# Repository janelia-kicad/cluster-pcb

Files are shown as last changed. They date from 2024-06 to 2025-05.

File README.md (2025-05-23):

- [Repository Info](#orgbacf8f6)
- [Images](#org53d800a)
- [Schematic](#org38f91d3)
- [PCB](#org650b85d)
- [Bill of Materials](#org1cf7621)
- [Development](#org0d98822)

    <!-- This file is generated automatically from metadata -->
    <!-- File edits may be overwritten! -->

# Repository Info

-   Project Name: cluster-pcb
-   Synopsis: PCB for each cluster of prisms in the Voigts Lab honeycomb maze.
-   Documentation Version: 2.1.0
-   Pcb Version: 2.1
-   Enclosure Version: 1.0
-   Supplemental BOM Version: 2.1.0
-   Release Date: 2025-05-23
-   Creation Date: 2024-06-28
-   Kicad Version: 9.0
-   License: BSD-3-Clause
-   URL: <https://github.com/janelia-kicad/cluster-pcb>
-   Author: Peter Polidoro
-   Email: peter@polidoro.io
-   Copyright: 2025 Howard Hughes Medical Institute
-   References:
    -   <https://github.com/janelia-kicad/prism-pcb>
    -   [W5500-EVB-Pico](https://docs.wiznet.io/Product/iEthernet/W5500/w5500-evb-pico)

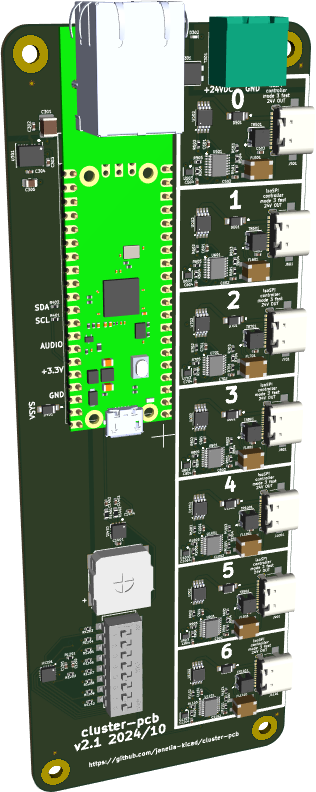
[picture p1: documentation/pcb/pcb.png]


# Images

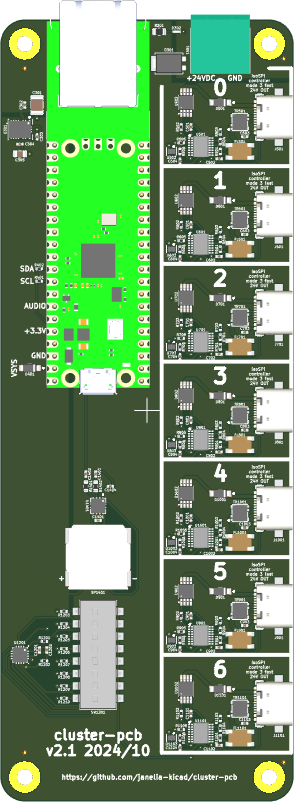
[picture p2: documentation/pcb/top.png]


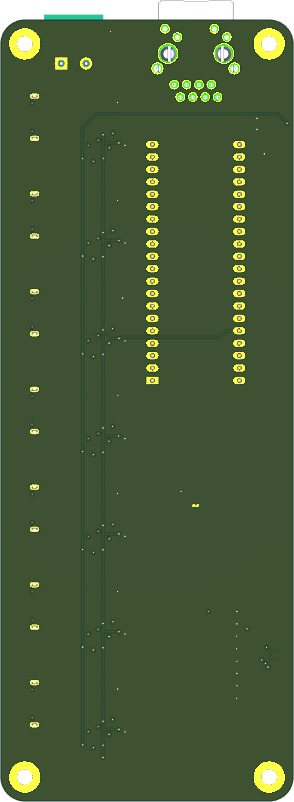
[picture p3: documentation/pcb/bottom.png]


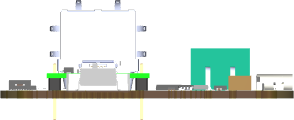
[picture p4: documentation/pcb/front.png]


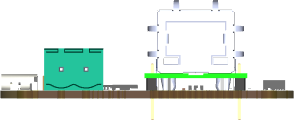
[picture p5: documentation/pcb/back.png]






# Schematic

[./documentation/schematic/cluster-pcb.pdf](./documentation/schematic/cluster-pcb.pdf)





























# PCB











# Bill of Materials

## Board

| Item | Synopsis                                  | Manufacturer Part Number | Manufacturer                         | Quantity | Reference(s)                                                                                                                    | Package            |
|---- |----------------------------------------- |------------------------ |------------------------------------ |-------- |------------------------------------------------------------------------------------------------------------------------------- |------------------ |
| 1    | 50V 3.3uF                                 | FS32X335K500EGG          | PSA(Prosperity Dielectrics)          | 1        | C301                                                                                                                            | 1210               |
| 2    | CAP CER 0.1UF 100V X5R                    | GRM155R62A104KE14D       | Murata Electronics                   | 24       | C302 C501 C502 C504 C601 C602 C604 C701 C702 C704 C801 C802 C804 C901 C902 C904 C1001 C1002 C1004 C1101 C1102 C1104 C1201 C1202 | 0402               |
| 3    | CAP CER 1UF 25V X5R                       | GRT155R61E105KE01D       | Murata Electronics                   | 2        | C303 C304                                                                                                                       | 0402               |
| 4    | CAP CER 47UF 10V X5R                      | CGA0805X5R476M100MT      | HRE                                  | 1        | C305                                                                                                                            | 0805               |
| 5    | CAP CER 27pF 50V 5%                       | 0402CG270J500NT          | FH (Guangdong Fenghua Advanced Tech) | 7        | C503 C603 C703 C803 C903 C1003 C1103                                                                                            | 0402               |
| 6    | CAP CER 1UF 35V X5R                       | CL05A105KL5NRNC          | Samsung Electro-Mechanics            | 1        | C1401                                                                                                                           | 0402               |
| 7    | CAP CER 0.22UF 25V X6S                    | GRT155C81E224KE01D       | Murata Electronics                   | 3        | C1402 C1403 C1404                                                                                                               | 0402               |
| 8    | 50V 15A PowerDI-5 Super Barrier Rectifier | SBRT15U50SP5-13          | Diodes Incorporated                  | 1        | D301                                                                                                                            | PowerDI-5          |
| 9    | LED RED CLEAR CHIP SMD                    | APHHS1005SURCK           | Kingbright                           | 1        | D302                                                                                                                            | 0402               |
| 10   | DIODE SCHOTTKY 20V 1A                     | MBR120VLSFT1G            | onsemi                               | 8        | D401 D501 D601 D701 D801 D901 D1001 D1101                                                                                       | SOD-123FL          |
| 11   | CMC 22UH 200MA 2LN 1.2KOHM SMD            | ACT45B-220-2P-TL003      | TDK                                  | 7        | FL501 FL601 FL701 FL801 FL901 FL1001 FL1101                                                                                     | 1812               |
| 12   | USB Type-C 2.0 16P 5A                     | GT-USB-7047C             | G-Switch                             | 7        | J501 J601 J701 J801 J901 J1001 J1101                                                                                            | SMD                |
| 13   | RA73F 2A 2K32 0.1% 5K RL                  | RA73F2A2K32BTD           | TE Connectivity Passive Product      | 1        | R301                                                                                                                            | 0805               |
| 14   | RES SMD 1.8K OHM 5% 100mW                 | ERJ2GEJ182X              | PANASONIC                            | 16       | R401 R402 R505 R506 R605 R606 R705 R706 R805 R806 R905 R906 R1005 R1006 R1105 R1106                                             | 0402               |
| 15   | RES SMD 100 OHM 1% 62.5mW                 | 0402WGF1000TCE           | UNI-ROYAL(Uniroyal Elec)             | 7        | R501 R601 R701 R801 R901 R1001 R1101                                                                                            | 0402               |
| 16   | RES SMD 4.7K OHM 1% 6.25mW                | 0402WGF4701TCE           | UNI-ROYAL(Uniroyal Elec)             | 7        | R502 R602 R702 R802 R902 R1002 R1102                                                                                            | 0402               |
| 17   | RES SMD 1.4K OHM 1% 62.5mW                | RC0402FR-071K4L          | YAGEO                                | 7        | R503 R603 R703 R803 R903 R1003 R1103                                                                                            | 0402               |
| 18   | RES SMD 604 OHM 1% 100mW                  | ERJ2RKF6040X             | PANASONIC                            | 7        | R504 R604 R704 R804 R904 R1004 R1104                                                                                            | 0402               |
| 19   | RES SMD 10K OHM 5% 1/10W                  | ERJ2GEJ103X              | PANASONIC                            | 10       | R1201 R1202 R1203 R1204 R1205 R1206 R1207 R1208 R1209 R1210                                                                     | 0402               |
| 20   | RES SMD 40k OHM 1% 100mW                  | SCR0603F40K              | VO                                   | 2        | R1401 R1402                                                                                                                     | 0603               |
| 21   | SPEAKER 8OHM 700MW                        | KLJ-01304T-08R07W        | KELIKING                             | 1        | SP1401                                                                                                                          |                    |
| 22   | SWITCH SLIDE DIP SPST 0.025A 24V          | SDA08H1SBDR              | C&K                                  | 1        | SW1201                                                                                                                          | SMD                |
| 23   | TERM BLOCK HDR 2POS 90DEG 5.08MM          | 1757242                  | Phoenix Contact                      | 1        | T301                                                                                                                            | Push-Pull P=5.08mm |
| 24   | Pulse Transformer 120uH 1CT:1CT           | FB020G00                 | Dongguan Mentech Optical & Magnetic  | 7        | TR501 TR601 TR701 TR801 TR901 TR1001 TR1101                                                                                     | SMD-6P 3.5x3.2mm   |
| 25   | DC-DC 5V 600mA Output 3-65V Input         | TPSM365R6V5RDNR          | Texas Instruments                    | 1        | U301                                                                                                                            | QFN-11(3.5x4.5)    |
| 26   | SPI Isolator                              | LTC6820HMS#3ZZTRPBF      | Analog Devices                       | 7        | U501 U601 U701 U801 U901 U1001 U1101                                                                                            | MSOP-16            |
| 27   | IC BUFF NON-INVERT 1.65-5.5V              | SN74LVC1G125DRYR         | Texas Instruments                    | 7        | U503 U603 U703 U803 U903 U1003 U1103                                                                                            | USON-6(1x1.5)      |
| 28   | IC XPNDR 400KHZ I2C SMBUS                 | TCA6408ARGTR             | Texas Instruments                    | 1        | U1201                                                                                                                           | QFN-16-EP(3x3)     |
| 29   | IC AMP CLASS AB MONO 1.7W                 | TPA6204A1DRBR            | Texas Instruments                    | 1        | U1401                                                                                                                           | QFN-8-EP(3x3)      |
|      | IC PWR DRIVER N-CHAN 1:1                  |                          | Texas Instruments                    | 7        | U502 U602 U702 U802 U902 U1002 U1102                                                                                            | EMSOP-8-EP         |

## Supplemental

| Item | Synopsis                        | Manufacturer Part Number | Manufacturer    | Quantity | Cost  | Total |
|---- |------------------------------- |------------------------ |--------------- |-------- |----- |----- |
| 1    | TERM BLOCK PLUG 2POS STR 5.08MM | 1758364                  | Phoenix Contact | 1        | 1.63  | 1.63  |
| 2    | CONN FERRULE DIN 16AWG BLACK    | 3200043                  | Phoenix Contact | 4        | 0.14  | 0.56  |
| 3    | POWER CABLE BULK SJT 16/3       | H-137                    | GlobTek, Inc.   | 1        | 2.40  | 2.40  |
| 4    | W5100S-EVB-PICO RP2040 W5100S   | W5100S-EVB-PICO          | WIZnet          | 1        | 9.95  | 9.95  |
| 5    | Supplemental BOM Version: 2.1.0 |                          |                 |          | Total | 14.54 |

# Development

## Install Guix

[Install Guix](https://guix.gnu.org/manual/en/html_node/Binary-Installation.html)

## Generate Output from KiCad

### Remove previous versions

```sh
rm -rf ./documentation/3dmodels/* && rm -rf ./documentation/bom/* && rm -rf ./documentation/fabrication/* && rm -rf ./documentation/pcb/* && rm -rf ./documentation/schematic/*pcb
```

### Images

1.  3D Viewer

    Output directory: ../documentation/pcb
    
    -   pcb.png
    -   top.png
    -   bottom.png
    -   front.png
    -   back.png
    -   left.png
    -   right.png

2.  Trim

        make trimmed-images

3.  Schematic PDF

    File -> Plot
    
    Output directory: ../documentation/schematic
    
    Plot All Pages
    
    -   Output format PDF
    -   Page Size = Schematic size
    -   Plot drawing sheet
    -   Output mode = Color
    -   Color theme = KiCad Default
    -   Default line width = 0.006 in

4.  Schematic SVG

    File -> Plot
    
    Output directory: ../documentation/schematic
    
    Plot All Pages
    
    -   Output format SVG
    -   Page Size = Schematic size
    -   Plot drawing sheet
    -   Output mode = Color
    -   Color theme = Solarized Light
    -   Default line width = 0.012 in

5.  PCB SVG

    Add Edge.Cuts, holes, and dimensions to User.Drawings
    
    File -> Plot
    
    Output directory: ../documentation/pcb
    
    -   Plot format SVG
    -   Include Layers
        -   User.Drawings
        -   F.Silkscreen
        -   B.Silkscreen
        -   F.Fab
        -   B.Fab
    -   Plot on All Layers
        -   Edge.Cuts
    -   Plot footprint values
    -   Plot reference designators
    -   SVG Options
        -   Precision = 4
        -   Output mode = color
    
        make cropped-svg

### Fabrication Files

1.  Gerbers

    File -> Fabrication Outputs -> Gerbers (.gbr)
    
    Output directory: ../documentation/fabrication/gerbers
    
    Include Layers:
    
    -   F.Cu
    -   F.Paste
    -   F.Silks
    -   F.Mask
    -   F.Fab
    -   B.Cu
    -   B.Paste
    -   B.Silks
    -   B.Mask
    -   B.Fab
    -   Edge.Cuts - (contain the board outline/cutouts.)
    -   In1.Cu, In2.Cu … - (needed for 4/6 layer designs.)
    
    Options:
    
    -   Select Plot reference designators, otherwise designators will not appear on silkscreen layers.
    -   Select Check zone fills before plotting
    -   Select Use Protel filename extensions, this is recommended as JLCPCB prefers Protel filename extensions.
    -   Select Subtract soldermask from silkscreen, this ensures no silkscreen on pads.
    -   Coordinate format 4.6 unit mm

2.  Drill and Map Files

    Output directory: ../documentation/fabrication/gerbers
    
    Options:
    
    -   Excellon drill file format
    -   Check Use alternate drill mode for "Oval Holes Drill Mode".
    -   Check Absolute for "Drill Origin".
    -   Check Millimeters for "Drill Units".
    -   Check Decimal format for "Zeros Format".
    -   Gerber X2 map file format
    
    Zip gerber files
    
        zip ./documentation/fabrication/gerbers.zip ./documentation/fabrication/gerbers/*

3.  BOM

    Generate BOM from schematic editor using blank command line to create bom xml file.

4.  POS

    File -> Fabrication Outputs -> Component Placement (.pos)
    
    Output directory: ../documentation/fabrication/
    
    Settings:
    
    -   Format = CSV
    -   Units = Millimeters
    -   Files = Single file for board
    -   Do not use drill/place file origin
    
    Modify pos files:
    
    -   Ref -> Designator
    -   PosX -> Mid X
    -   PosY -> Mid Y
    -   Rot -> Rotation
    -   Side -> Layer

5.  Step

    File -> Export -> Step
    
    Output directory: ../documentation/3dmodels/pcb.step
    
    -   Drill/place file origin
    -   Overwrite old file
    -   Standard Board outline chaining tolerance

## Edit metadata.org

    make metadata-edits

## Tangle metadata.org

    make metadata

## Edit project

    make kicad-edits
    exit

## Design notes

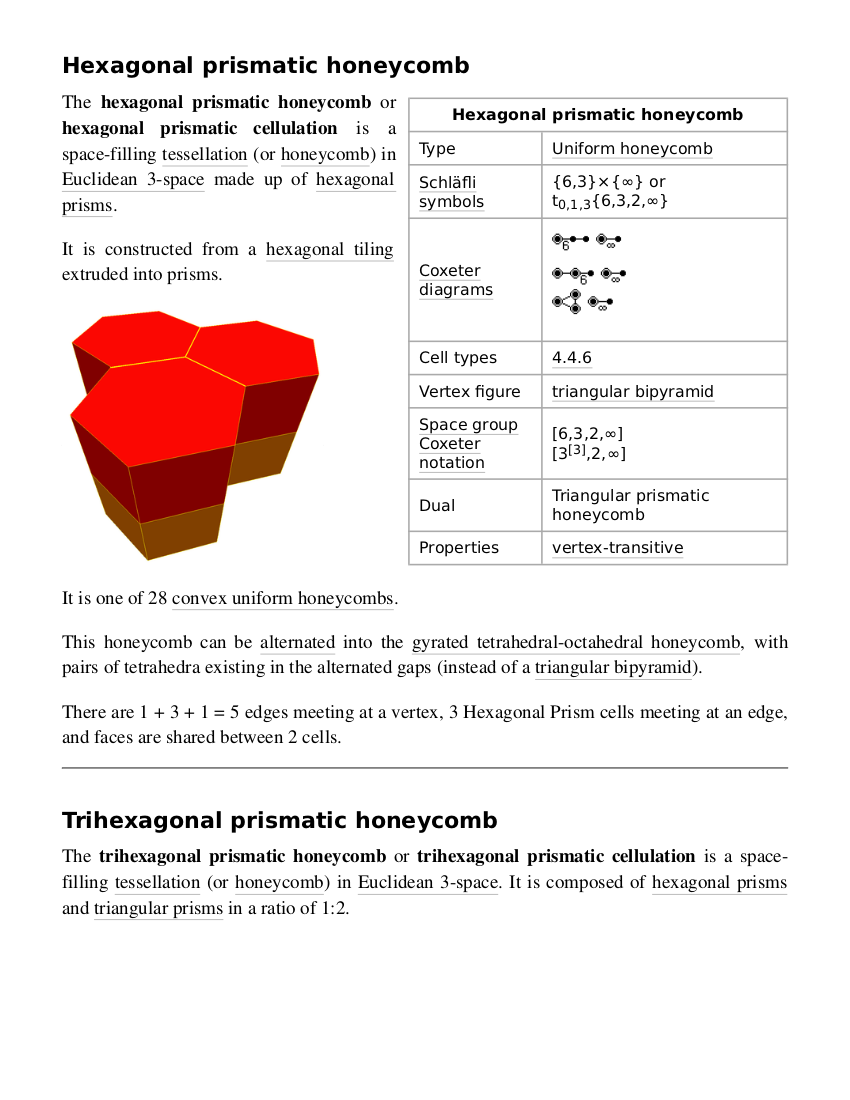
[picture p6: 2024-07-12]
documentation/images/honeycomb.png

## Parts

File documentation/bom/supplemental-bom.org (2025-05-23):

#+OPTIONS: toc:nil title:nil num:nil ^:nil
#+LATEX_HEADER: \usepackage{adjustbox}
#+LATEX_HEADER: \usepackage[margin=2cm]{geometry}
* Supplemental BOM
- Project Name: cluster-pcb
- Synopsis: PCB for each cluster of prisms in the Voigts Lab honeycomb maze.
- Release Date: 2025-05-23
- URL: https://github.com/janelia-kicad/cluster-pcb
- Author: Peter Polidoro
- Email: peter@polidoro.io
#+BEGIN_TABLE
#+LATEX: \adjustbox{max width=\linewidth}{
#+ATTR_LATEX: :center nil
| Item | Synopsis                                               | Manufacturer Part Number | Manufacturer    | Quantity |  Cost | Total |
|------+--------------------------------------------------------+--------------------------+-----------------+----------+-------+-------|
|    1 | TERM BLOCK PLUG 2POS STR 5.08MM                        | 1758364                  | Phoenix Contact |        1 |  1.63 |  1.63 |
|    2 | CONN FERRULE DIN 16AWG BLACK                           | 3200043                  | Phoenix Contact |        4 |  0.14 |  0.56 |
|    3 | POWER CABLE BULK SJT 16/3                              | H-137                    | GlobTek, Inc.   |        1 |  2.40 |  2.40 |
|    4 | W5100S-EVB-PICO RP2040 W5100S                          | W5100S-EVB-PICO          | WIZnet          |        1 |  9.95 |  9.95 |
|------+--------------------------------------------------------+--------------------------+-----------------+----------+-------+-------|
|    5 | Supplemental BOM Version: 2.1.0 |                          |                 |          | Total | 14.54 |
#+TBLFM: $1=@#-1::$7=$5*$6;%0.2f::@>$7=vsum(@2..@-1);%0.2f
#+LATEX: }
#+END_TABLE

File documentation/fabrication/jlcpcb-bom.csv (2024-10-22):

Comment | Designator | Footprint | LCSC
50V 3.3uF | C301 | 1210 | C1021610
CAP CER 0.1UF 100V X5R | C302 C501 C502 C504 C601 C602 C604 C701 C702 C704 C801 C802 C804 C901 C902 C904 C1001 C1002 C1004 C1101 C1102 C1104 C1201 C1202 | 0402 | C162178
CAP CER 1UF 25V X5R | C303 C304 | 0402 | C711085
CAP CER 47UF 10V X5R | C305 | 0805 | C6119904
CAP CER 27pF 50V 5% | C503 C603 C703 C803 C903 C1003 C1103 | 0402 | C1557
CAP CER 1UF 35V X5R | C1401 | 0402 | C307413
CAP CER 0.22UF 25V X6S | C1402 C1403 C1404 | 0402 | C126623
50V 15A PowerDI-5 Super Barrier Rectifier | D301 | PowerDI-5 | C211388
LED RED CLEAR CHIP SMD | D302 | 0402 | C2852592
DIODE SCHOTTKY 20V 1A | D401 D501 D601 D701 D801 D901 D1001 D1101 | SOD-123FL | C223608
CMC 22UH 200MA 2LN 1.2KOHM SMD | FL501 FL601 FL701 FL801 FL901 FL1001 FL1101 | 1812 | C88055
USB Type-C 2.0 16P 5A | J501 J601 J701 J801 J901 J1001 J1101 | SMD | C963218
RA73F 2A 2K32 0.1% 5K RL | R301 | 0805 | C3961061
RES SMD 1.8K OHM 5% 100mW | R401 R402 R505 R506 R605 R606 R705 R706 R805 R806 R905 R906 R1005 R1006 R1105 R1106 | 0402 | C409855
RES SMD 100 OHM 1% 62.5mW | R501 R601 R701 R801 R901 R1001 R1101 | 0402 | C25076
RES SMD 4.7K OHM 1% 6.25mW | R502 R602 R702 R802 R902 R1002 R1102 | 0402 | C25900
RES SMD 1.4K OHM 1% 62.5mW | R503 R603 R703 R803 R903 R1003 R1103 | 0402 | C375491
RES SMD 604 OHM 1% 100mW | R504 R604 R704 R804 R904 R1004 R1104 | 0402 | C2076855
RES SMD 10K OHM 5% 1/10W | R1201 R1202 R1203 R1204 R1205 R1206 R1207 R1208 R1209 R1210 | 0402 | C278577
RES SMD 40k OHM 1% 100mW | R1401 R1402 | 0603 | C3016445
SPEAKER 8OHM 700MW | SP1401 |  | C18186315
SWITCH SLIDE DIP SPST 0.025A 24V | SW1201 | SMD | C2799987
TERM BLOCK HDR 2POS 90DEG 5.08MM | T301 | Push-Pull P=5.08mm | C90074
Pulse Transformer 120uH 1CT:1CT | TR501 TR601 TR701 TR801 TR901 TR1001 TR1101 | SMD-6P 3.5x3.2mm | C19673866
DC-DC 5V 600mA Output 3-65V Input | U301 | QFN-11(3.5x4.5) | C19078014
SPI Isolator | U501 U601 U701 U801 U901 U1001 U1101 | MSOP-16 | C514444
IC BUFF NON-INVERT 1.65-5.5V | U503 U603 U703 U803 U903 U1003 U1103 | USON-6(1x1.5) | C527546
IC XPNDR 400KHZ I2C SMBUS | U1201 | QFN-16-EP(3x3) | C181499
IC AMP CLASS AB MONO 1.7W | U1401 | QFN-8-EP(3x3) | C12400
IC PWR DRIVER N-CHAN 1:1 | U502 U602 U702 U802 U902 U1002 U1102 | EMSOP-8-EP | C2653785

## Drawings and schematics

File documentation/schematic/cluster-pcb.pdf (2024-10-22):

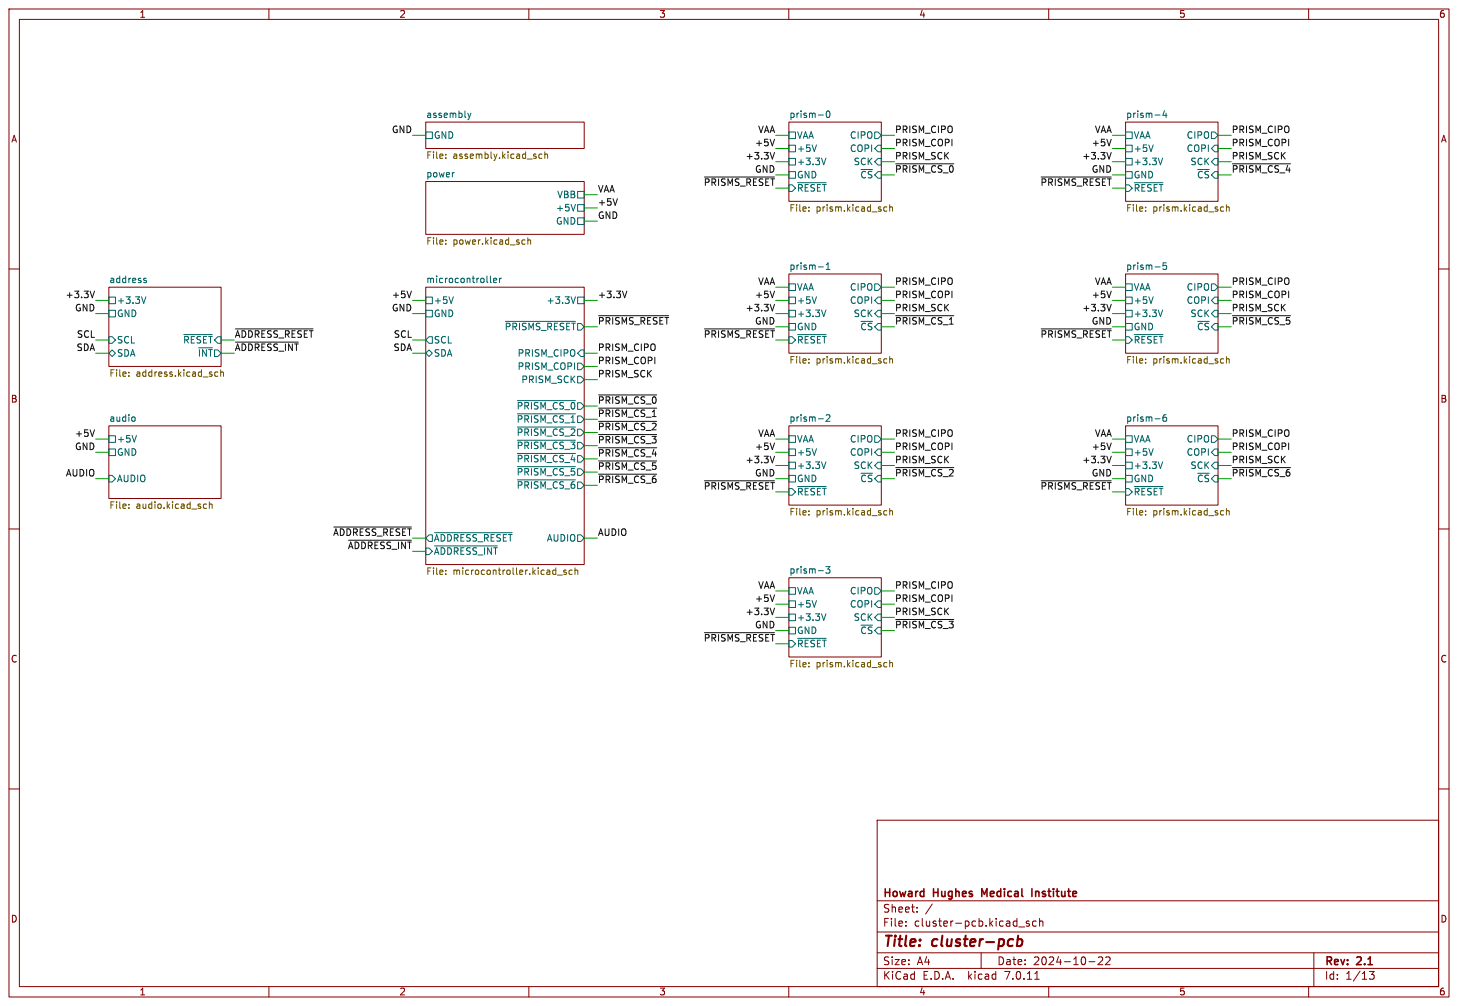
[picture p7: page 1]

~{PRISM_CS_6} microcontroller File: microcontroller.kicad_sch GND

prism-4 File: prism.kicad_sch GND

power File: power.kicad_sch SDA

prism-5 File: prism.kicad_sch GND

prism-3 File: prism.kicad_sch +5V GND

Id: 1/13 Title: cluster-pcb

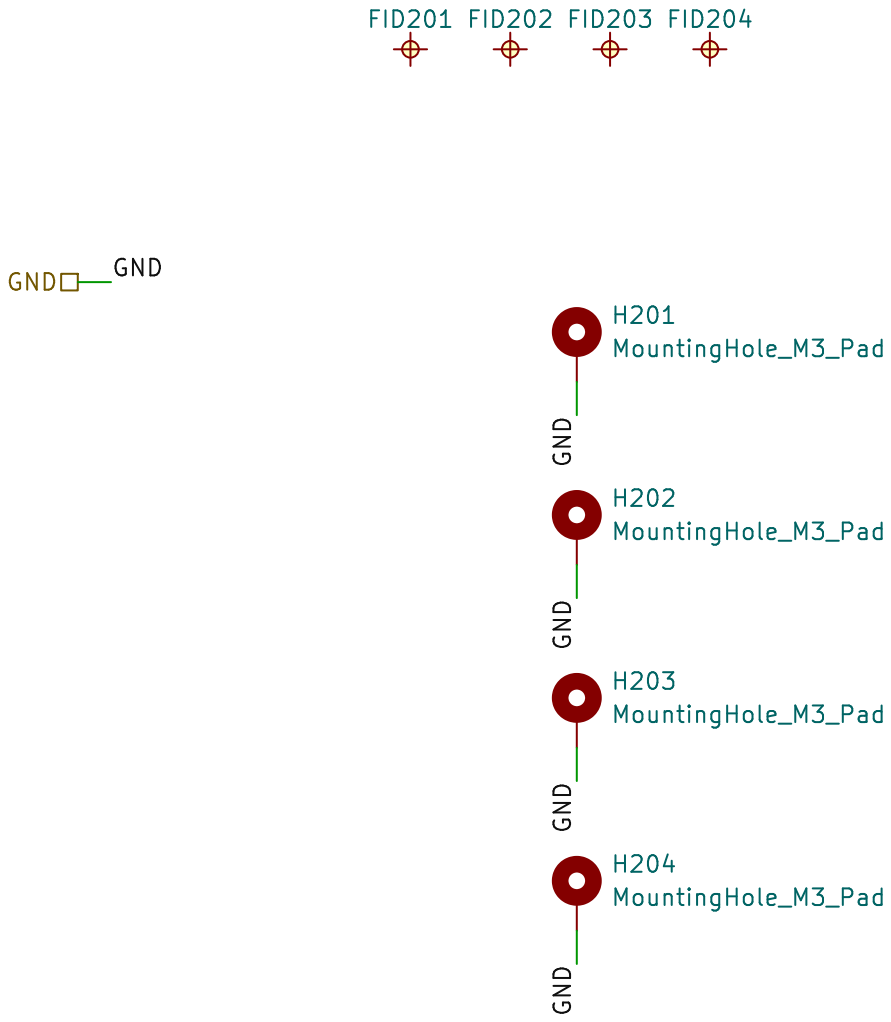
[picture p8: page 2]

Id: 2/13 Title: cluster-pcb

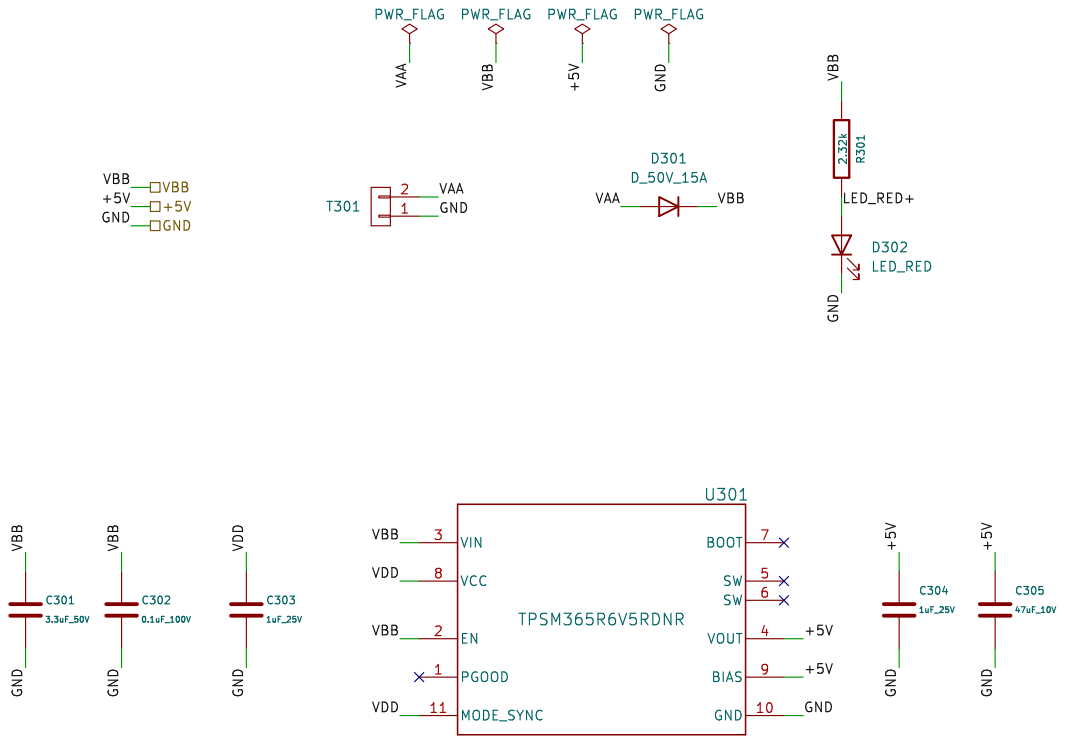
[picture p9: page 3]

Id: 3/13 Title: cluster-pcb

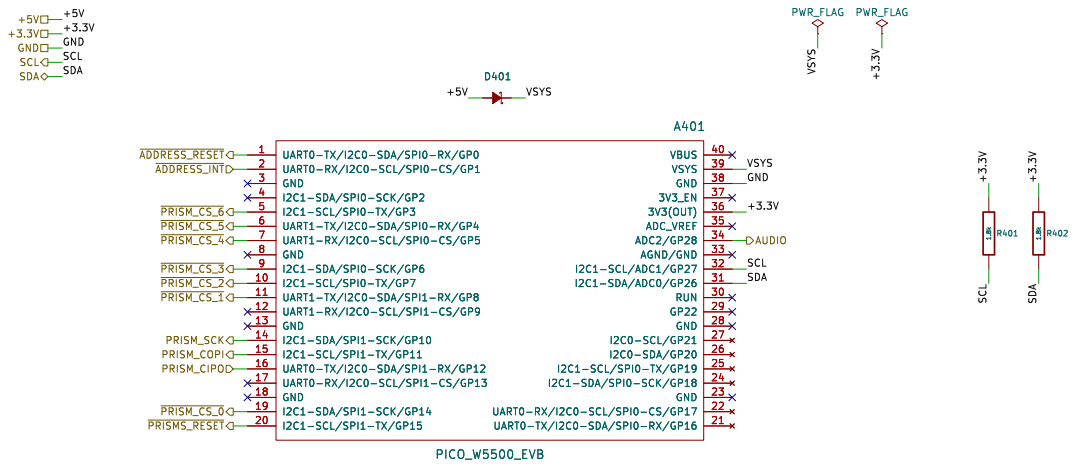
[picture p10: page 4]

Id: 4/13 Title: cluster-pcb

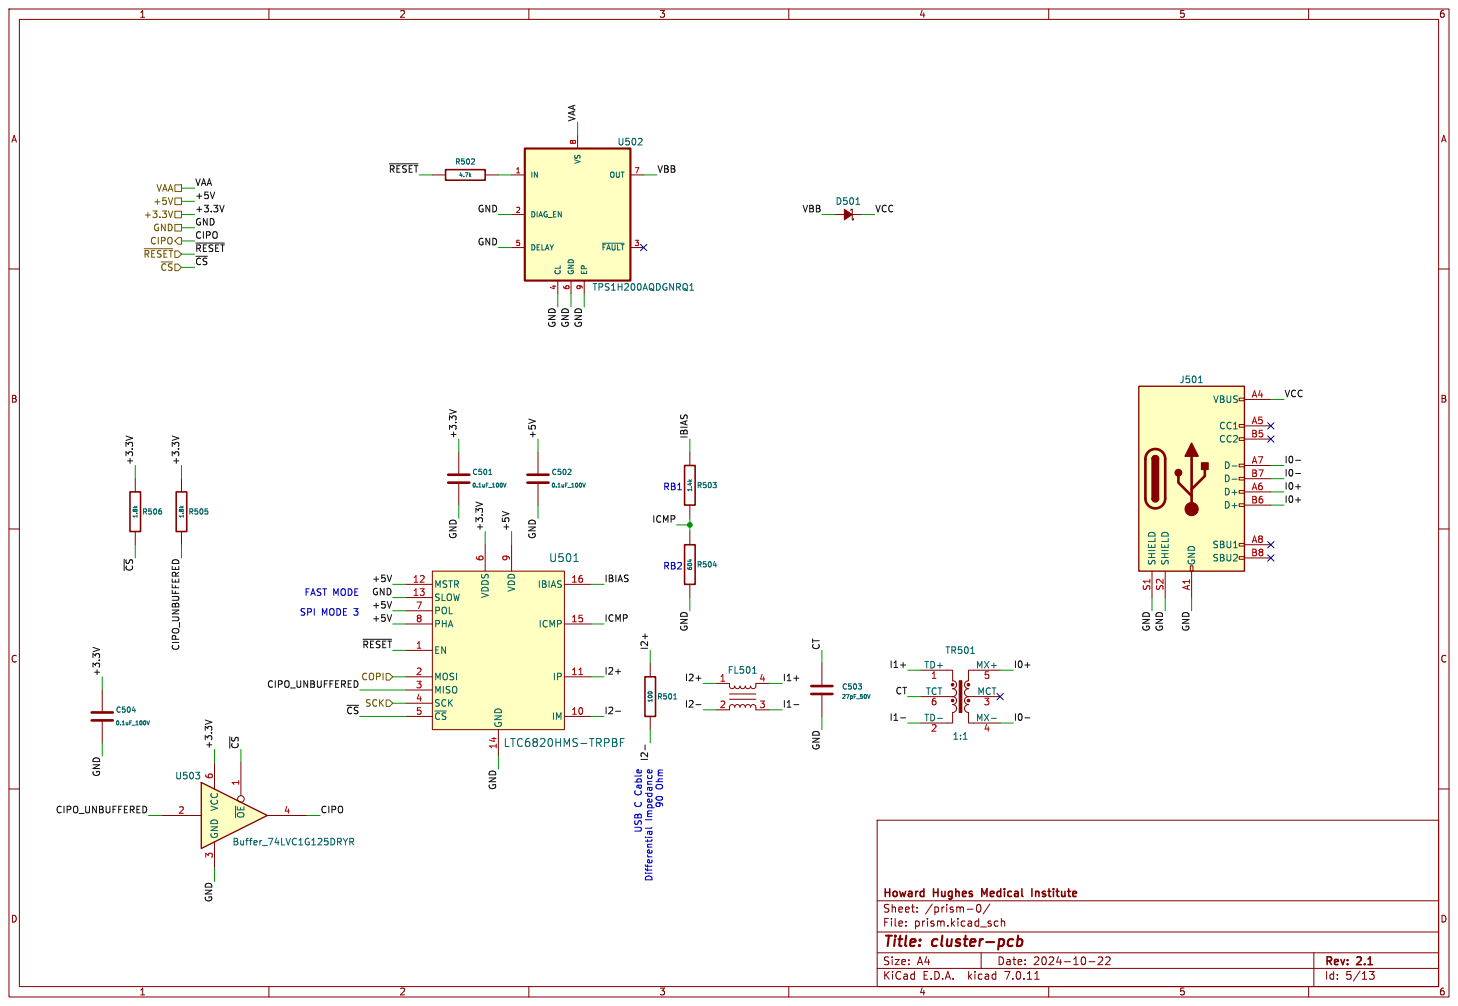
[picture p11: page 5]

Id: 5/13 Title: cluster-pcb

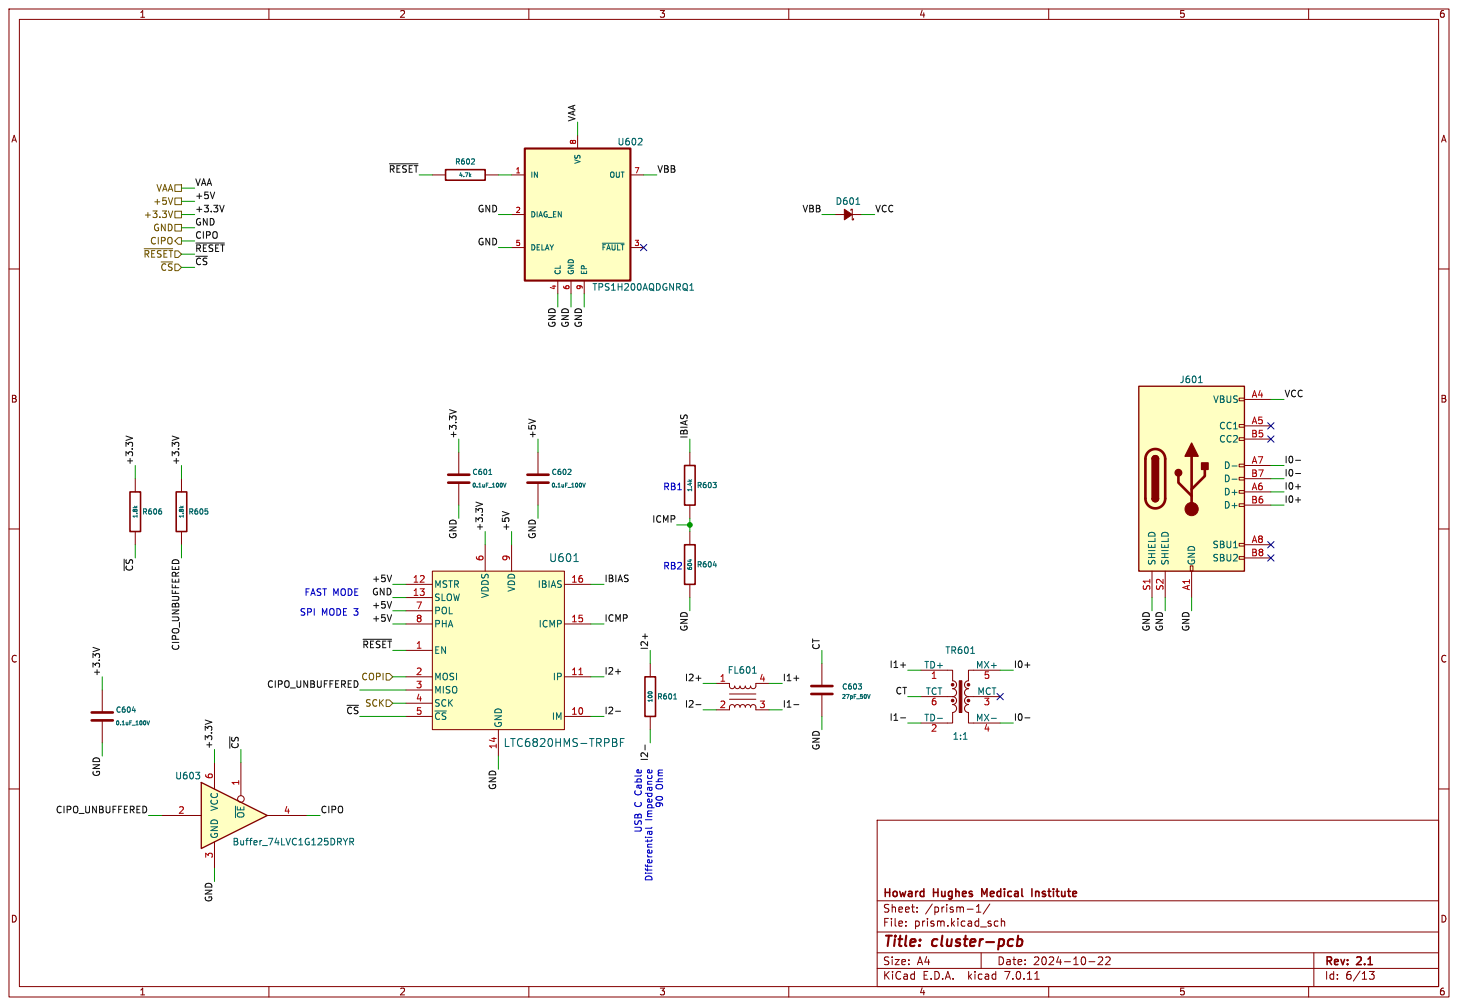
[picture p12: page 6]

Id: 6/13 Title: cluster-pcb

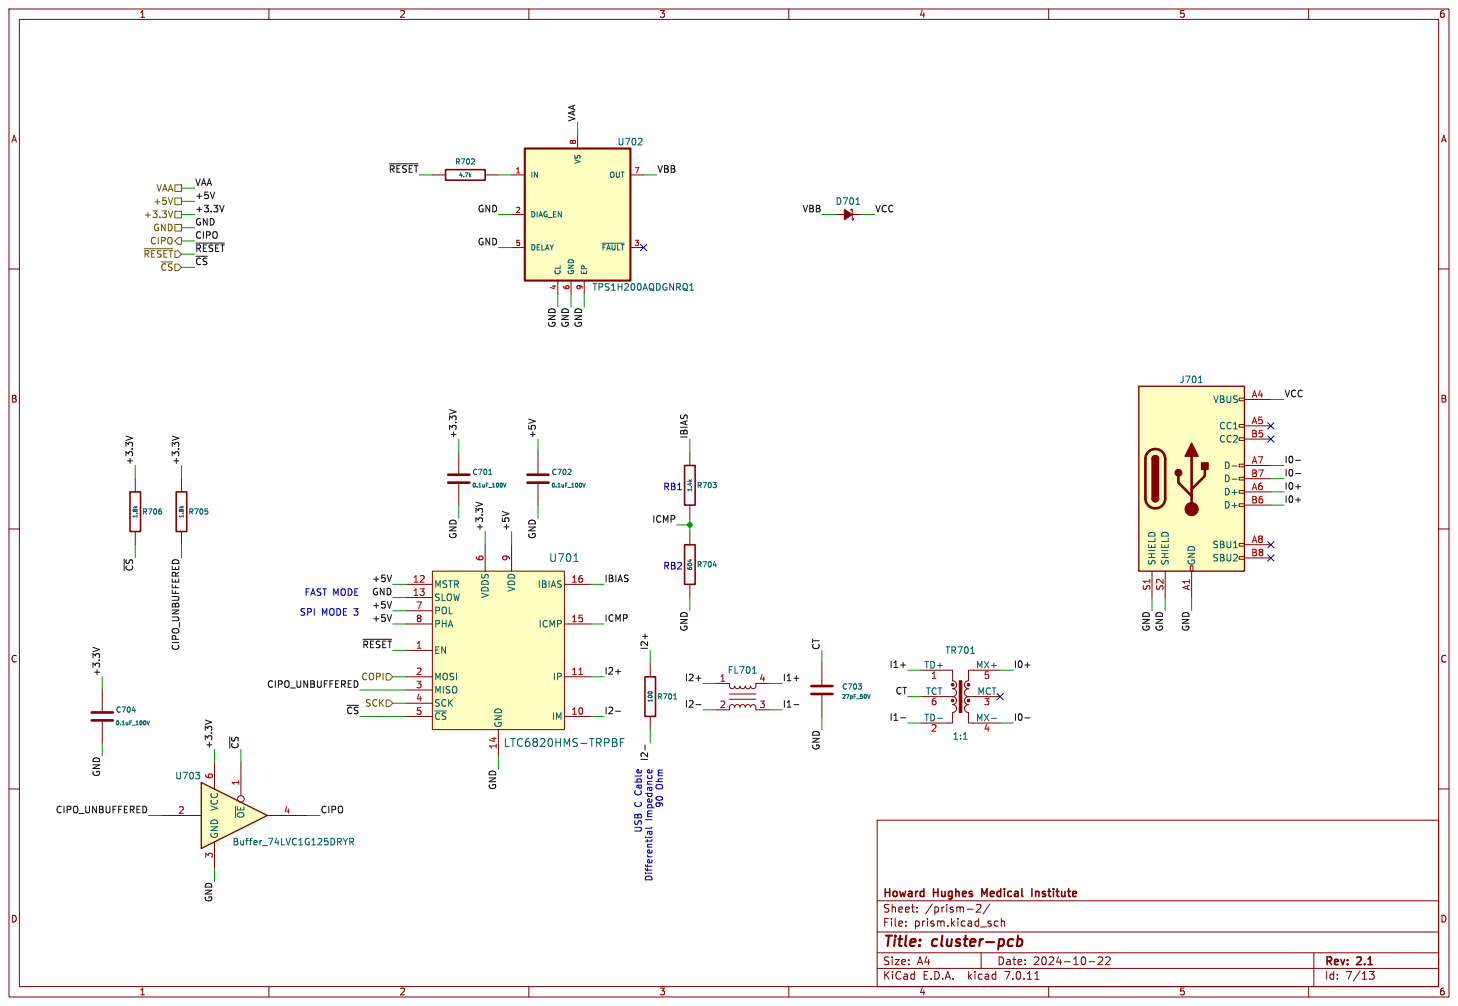
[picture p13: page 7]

Id: 7/13 Title: cluster-pcb

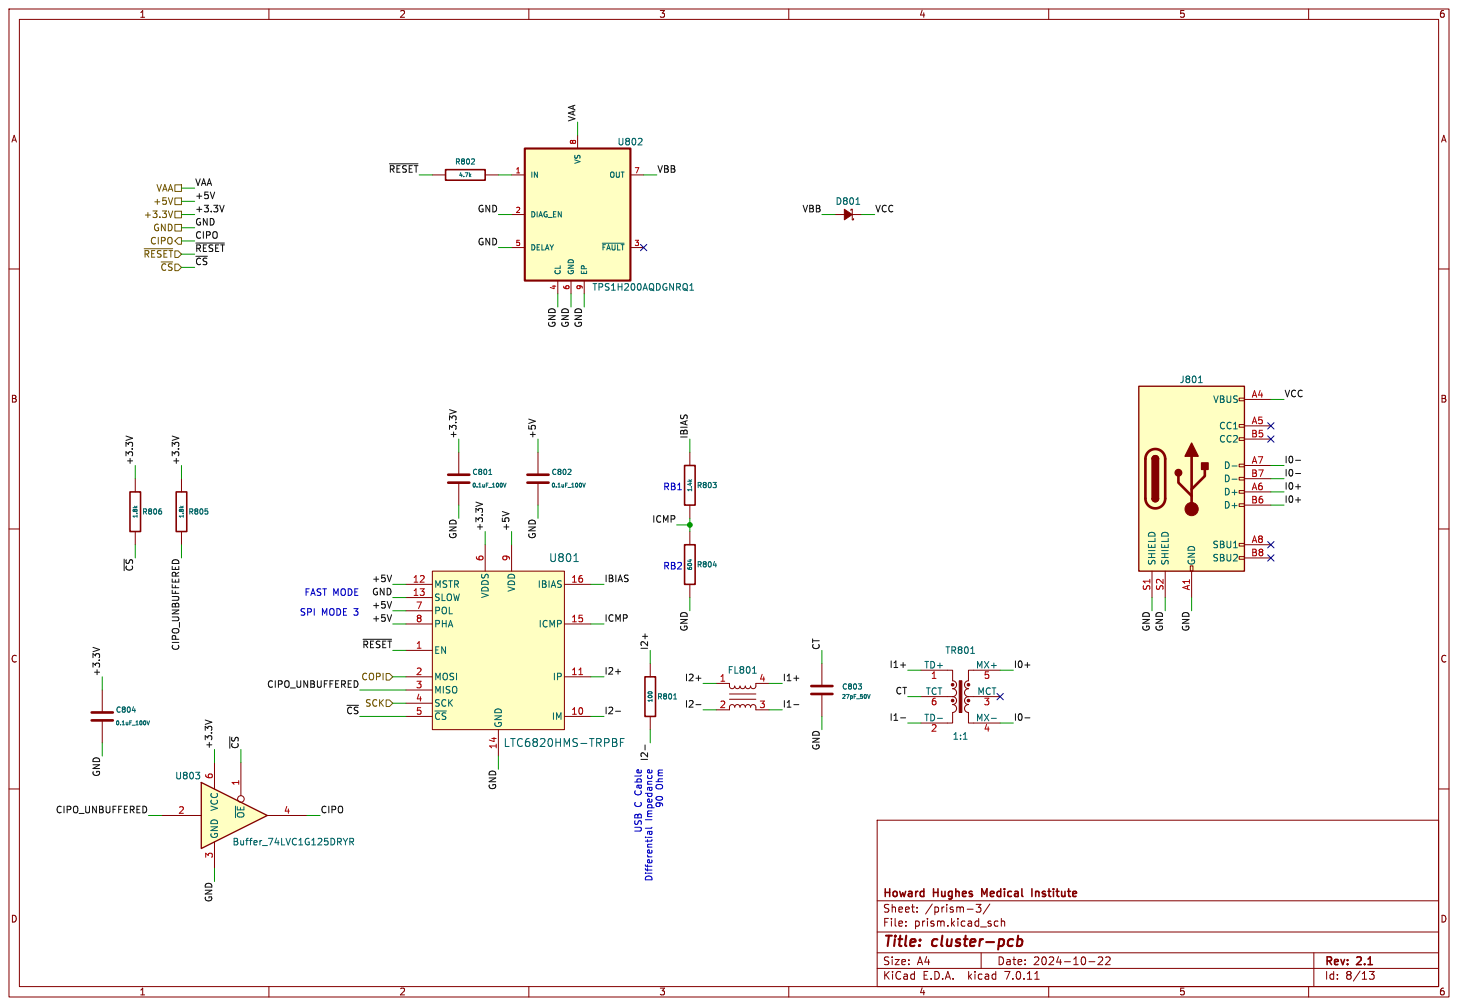
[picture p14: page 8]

Id: 8/13 Title: cluster-pcb

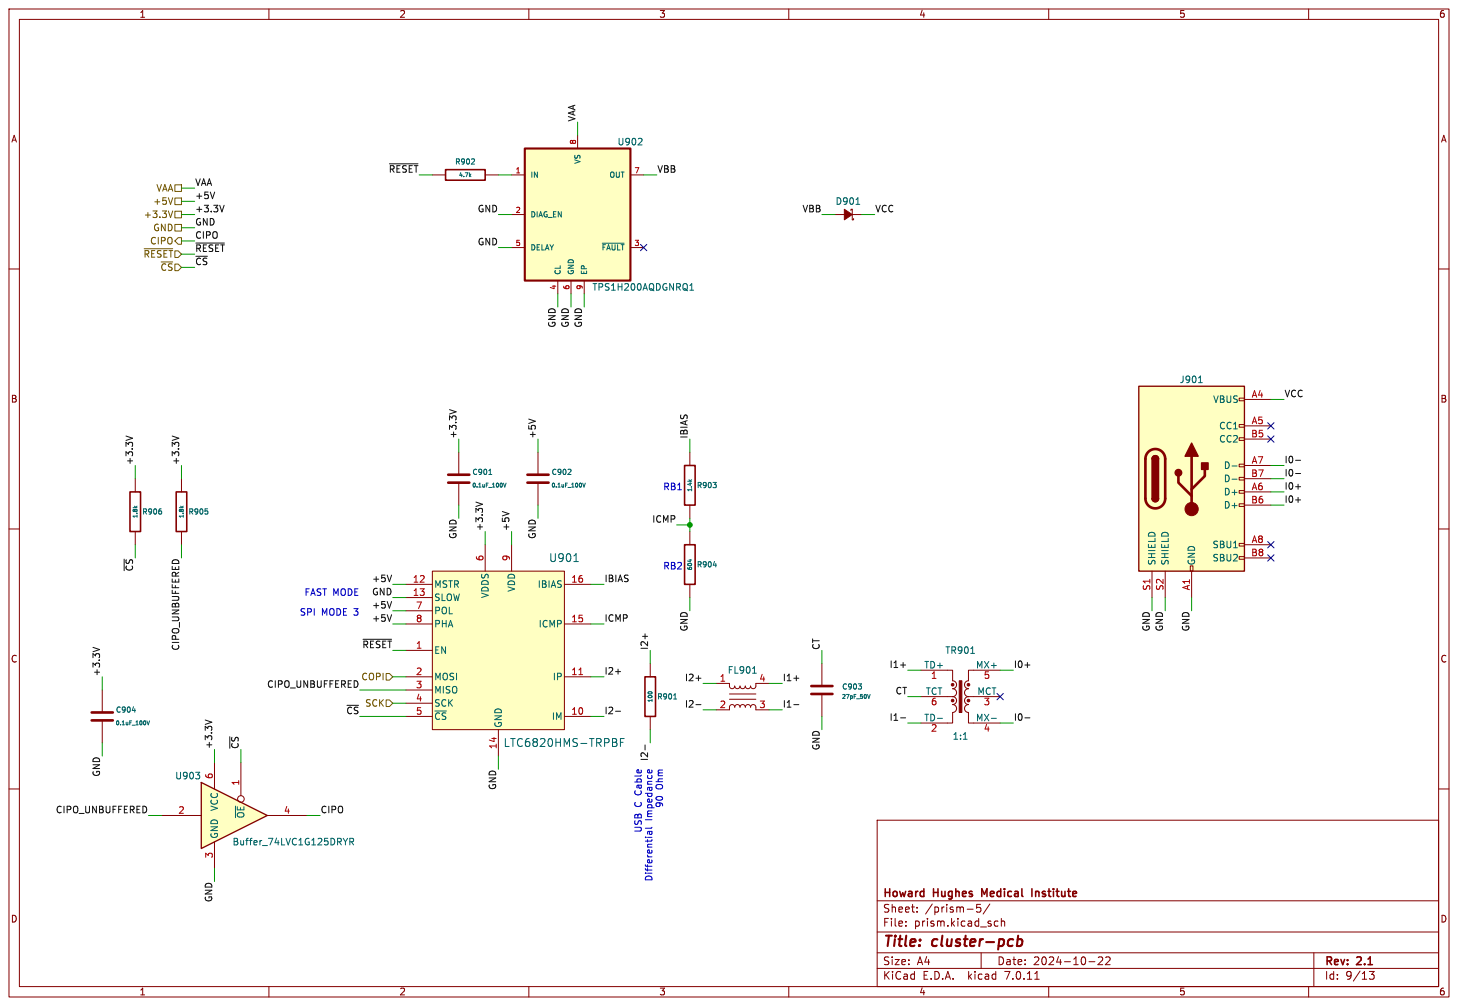
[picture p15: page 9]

Id: 9/13 Title: cluster-pcb

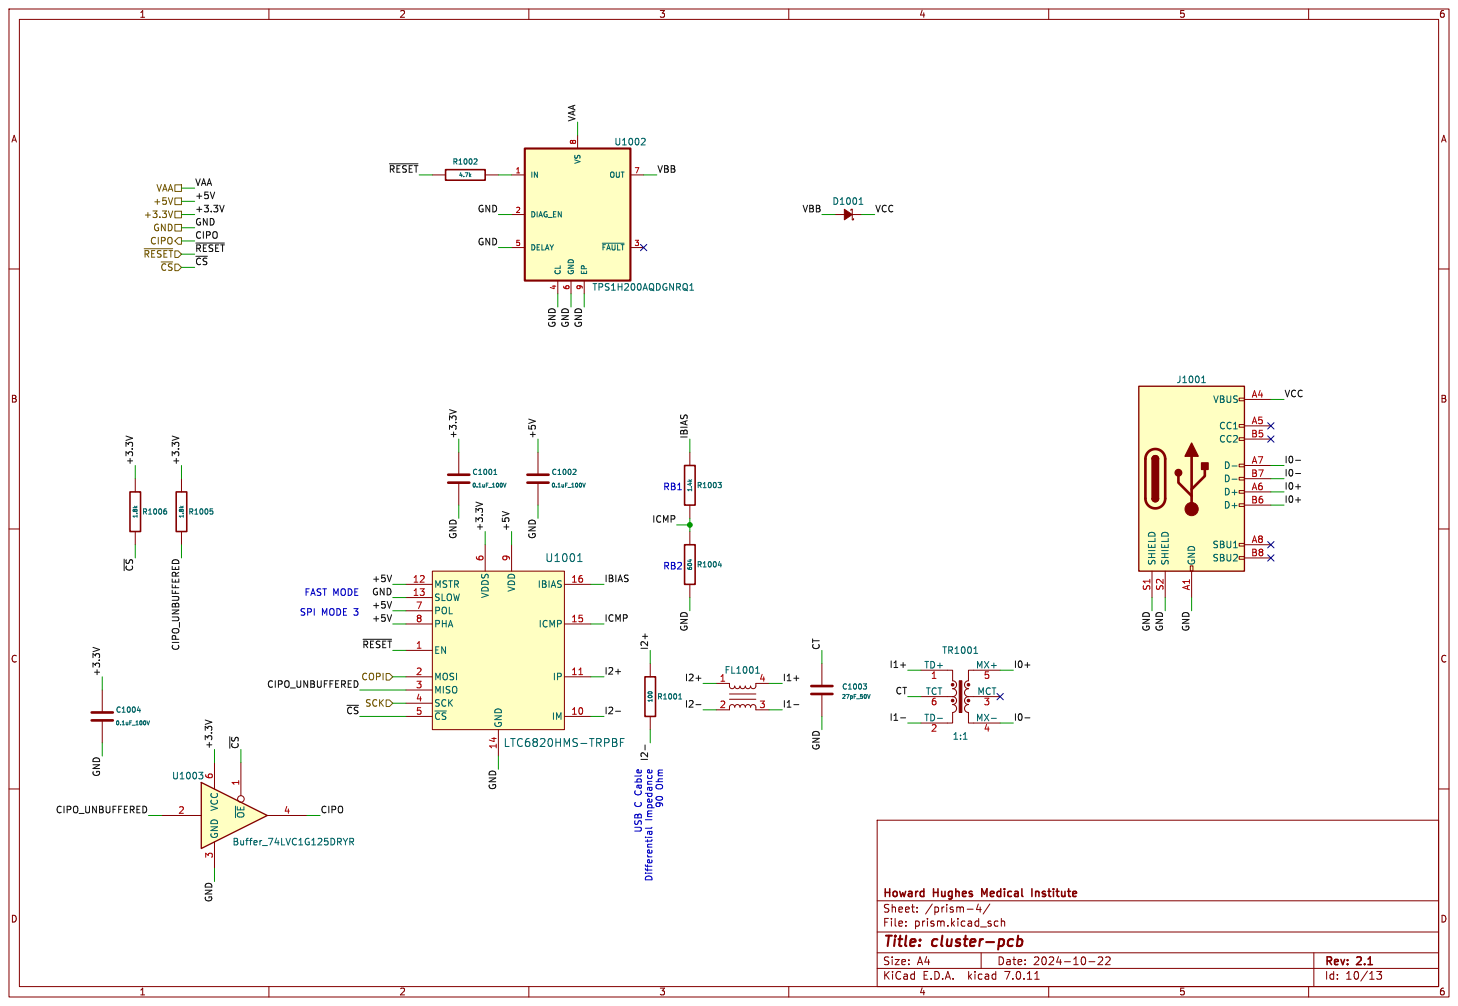
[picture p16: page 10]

Id: 10/13 Title: cluster-pcb

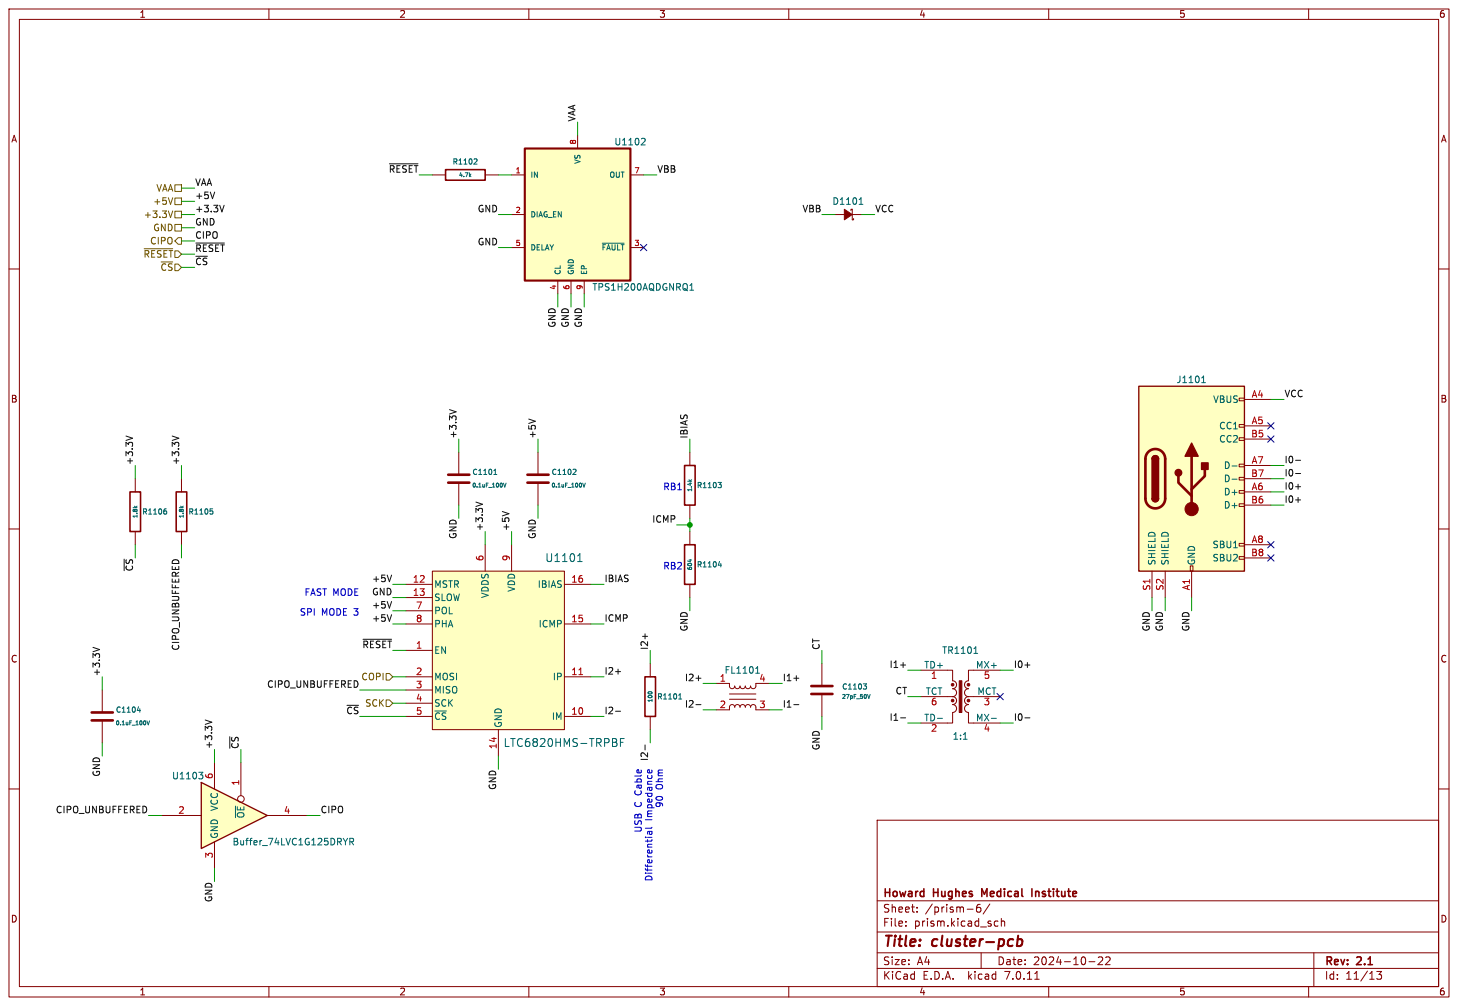
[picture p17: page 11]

Id: 11/13 Title: cluster-pcb

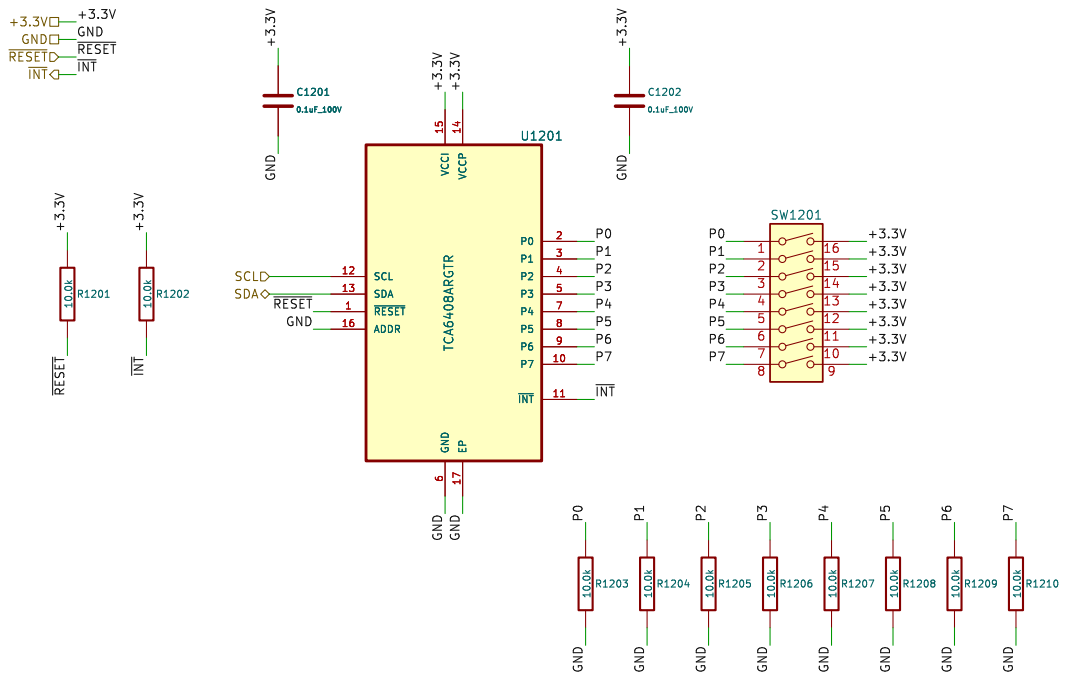
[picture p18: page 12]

Id: 12/13 Title: cluster-pcb


VO- VO+ VO- VO+ +5V GND GND GND BYPASS

Id: 14/13 Title: cluster-pcb

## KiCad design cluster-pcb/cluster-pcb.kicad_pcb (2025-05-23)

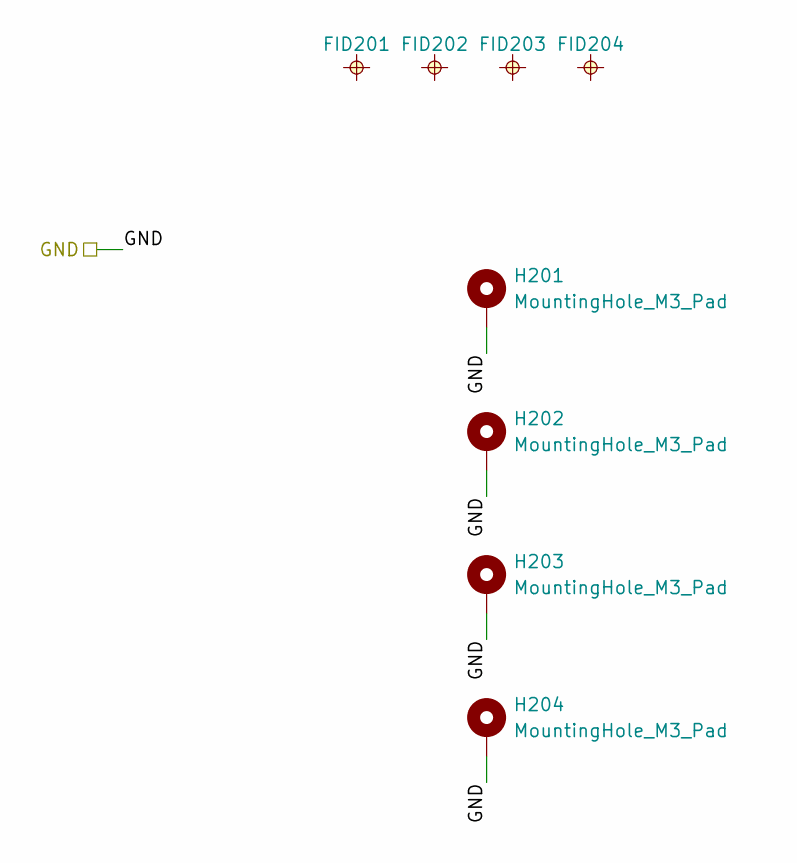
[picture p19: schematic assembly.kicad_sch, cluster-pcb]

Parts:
FID201, FID202, FID203, FID204: FIDUCIAL_0.5mm_MASK1mm; FIDUCIAL_0.5mm_Mask1mm
H201, H202, H203, H204: MountingHole_M3_Pad; MountingHole_3.2mm_M3_Pad

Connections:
/GND: H201.1, H202.1, H203.1, H204.1; also elsewhere on the board

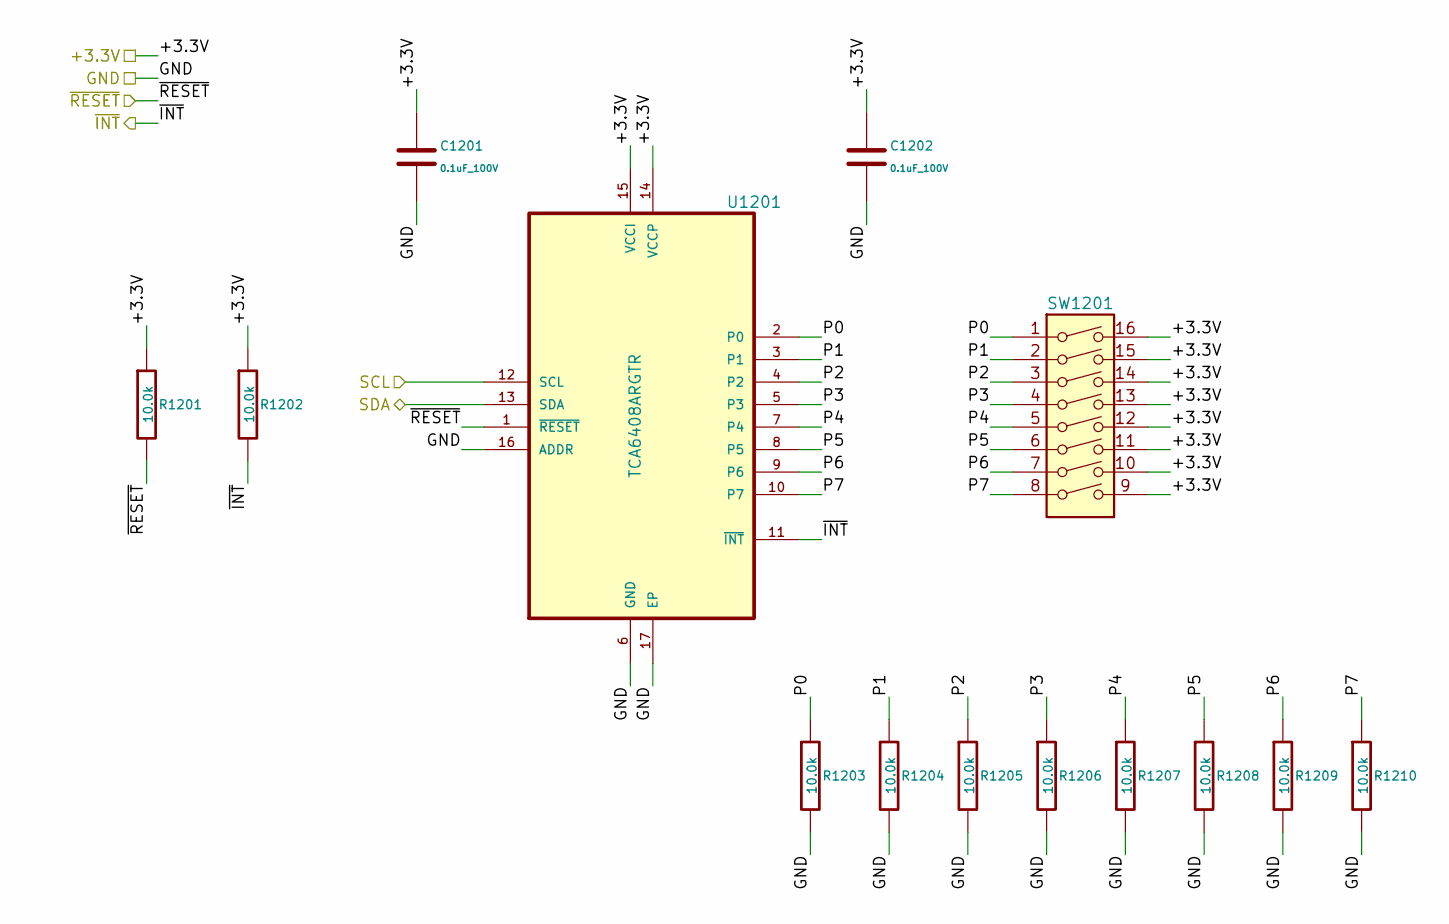
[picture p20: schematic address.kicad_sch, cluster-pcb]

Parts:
C1201, C1202: 0.1uF_100V; C_0402_1005Metric; Manufacturer Part Number GRM155R62A104KE14D; LCSC C162178
R1201, R1202, R1203, R1204, R1205, R1206, R1207, R1208, R1209, R1210: 10.0k; R_0402_1005Metric; Manufacturer Part Number ERJ2GEJ103X; LCSC C278577
SW1201: SW_DIP_x08_SDA08H1SBDR; SW_DIP_SPSTx08_Slide_SDA08H1SBDR; Manufacturer Part Number SDA08H1SBDR; LCSC C2799987
U1201: TCA6408ARGTR; QFN50P300X300X100-17N; Manufacturer Part Number TCA6408ARGTR; LCSC C181499

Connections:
/+3.3V: C1201.1, C1202.1, R1201.1, R1202.1, SW1201.9, SW1201.10, SW1201.11, SW1201.12, SW1201.13, SW1201.14, SW1201.15, SW1201.16, U1201.14 (VCCP), U1201.15 (VCCI); also elsewhere on the board
/GND: C1201.2, C1202.2, R1203.2, R1204.2, R1205.2, R1206.2, R1207.2, R1208.2, R1209.2, R1210.2, U1201.6 (GND), U1201.16 (ADDR), U1201.17 (EP); also elsewhere on the board
/SCL: U1201.12 (SCL); also elsewhere on the board
/SDA: U1201.13 (SDA); also elsewhere on the board
/address/P0: R1203.1, SW1201.1, U1201.2 (P0)
/address/P1: R1204.1, SW1201.2, U1201.3 (P1)
/address/P2: R1205.1, SW1201.3, U1201.4 (P2)
/address/P3: R1206.1, SW1201.4, U1201.5 (P3)
/address/P4: R1207.1, SW1201.5, U1201.7 (P4)
/address/P5: R1208.1, SW1201.6, U1201.8 (P5)
/address/P6: R1209.1, SW1201.7, U1201.9 (P6)
/address/P7: R1210.1, SW1201.8, U1201.10 (P7)
/~ADDRESS_INT: R1202.2, U1201.11 (~INT); also elsewhere on the board
/~ADDRESS_RESET: R1201.2, U1201.1 (~RESET); also elsewhere on the board

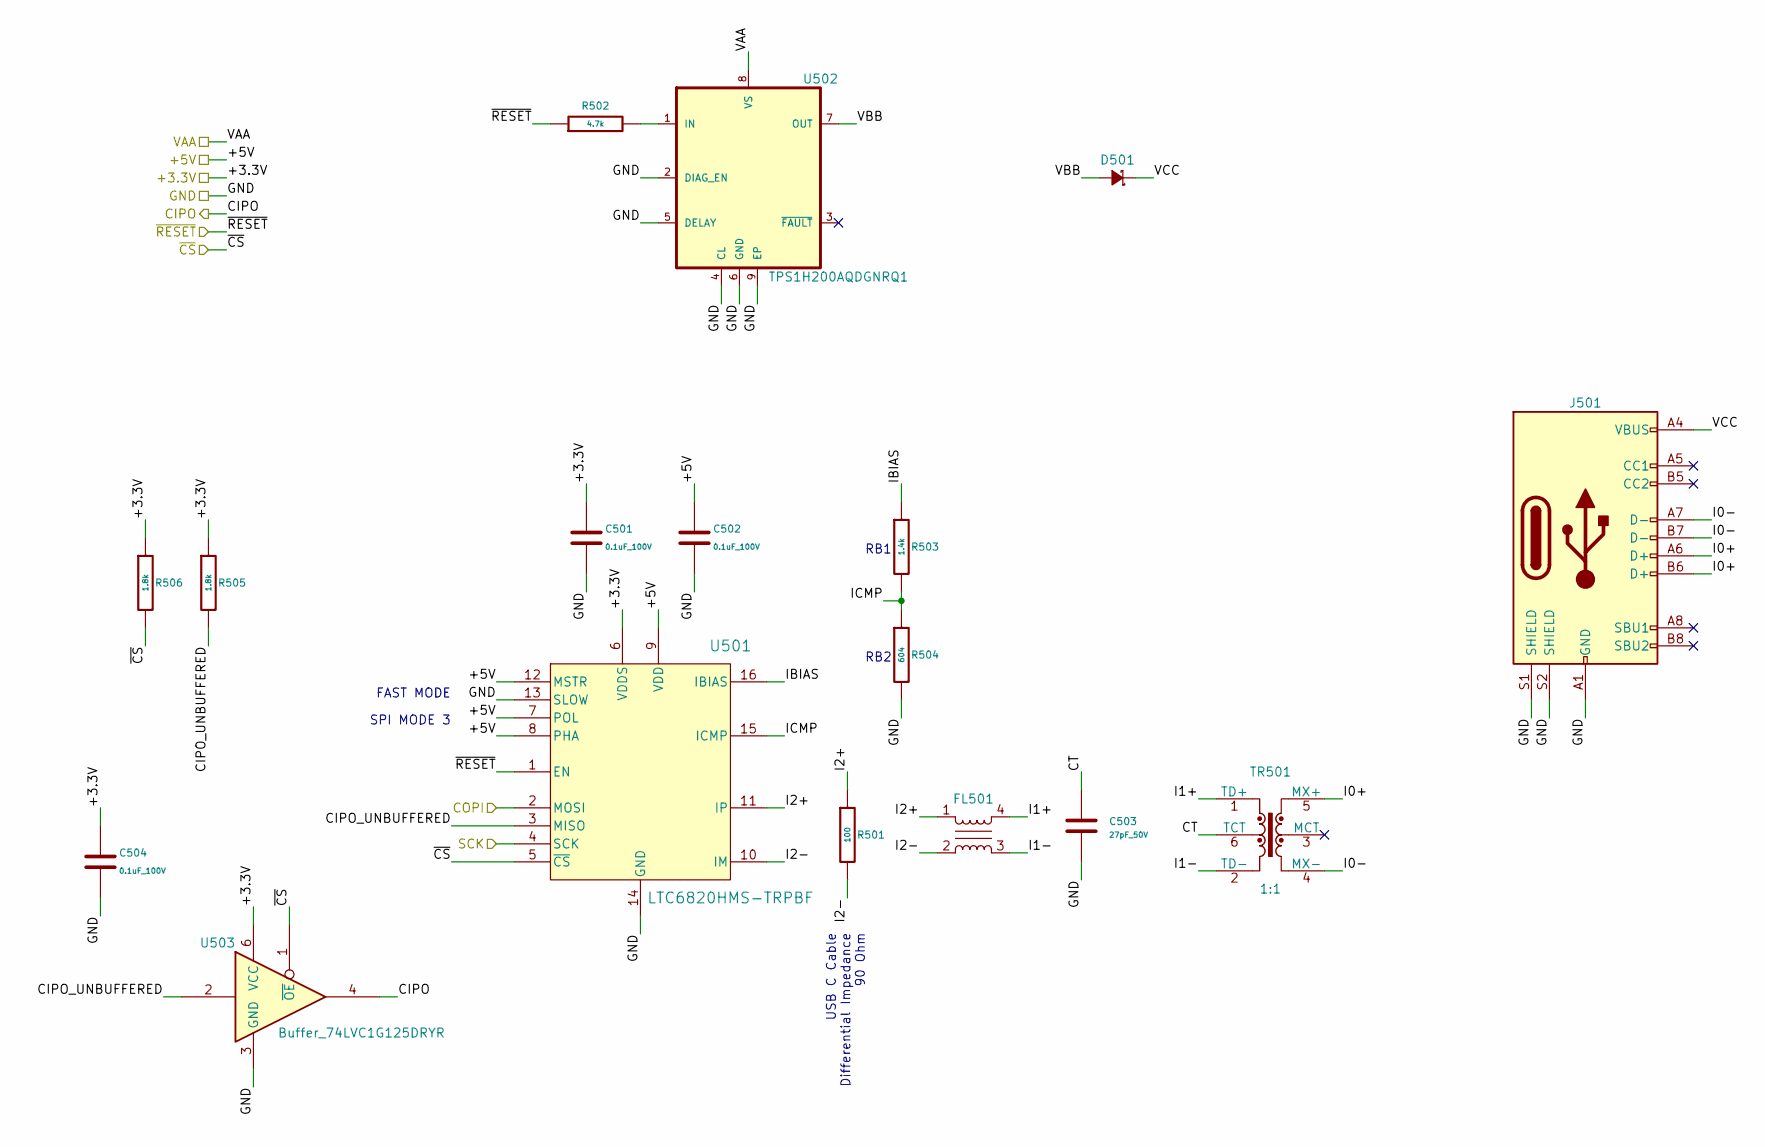
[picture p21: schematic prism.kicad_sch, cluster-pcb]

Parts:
C501, C502, C504: 0.1uF_100V; C_0402_1005Metric; Manufacturer Part Number GRM155R62A104KE14D; LCSC C162178
C503: 27pF_50V; C_0402_1005Metric; Manufacturer Part Number 0402CG270J500NT; LCSC C1557
D501: D_SCHOTTKY_20V_1A; SOD-123FL; Manufacturer Part Number DSK36; LCSC C106913
FL501: Choke_CMF_ACT45B-220-2P; SMD_0-2P-TL003_TDK-L; Manufacturer Part Number ACT45B-220-2P-TL003; LCSC C88055
J501: Connector_USB_C_Receptacle_USB2.0_16P_GT-USB-7047C; USB_C_Receptacle_GT-USB-7047C_16P_TopMnt_Horizontal; Manufacturer Part Number GT-USB-7047C; LCSC C963218
R501: 100; R_0402_1005Metric; Manufacturer Part Number 0402WGF1000TCE; LCSC C25076
R502: 4.7k; R_0402_1005Metric; Manufacturer Part Number 0402WGF4701TCE; LCSC C25900
R503: 1.4k; R_0402_1005Metric; Manufacturer Part Number RC0402FR-071K4L; LCSC C375491
R504: 604; R_0402_1005Metric; Manufacturer Part Number ERJ2RKF6040X; LCSC C2076855
R505, R506: 1.8k; R_0402_1005Metric; Manufacturer Part Number ERJ2GEJ182X; LCSC C409855
TR501: 1:1; FB020G00; Manufacturer Part Number FB020G00; LCSC C19673866
U501: LTC6820HMS-TRPBF; MS_05-08-1669_ADI; Manufacturer Part Number LTC6820HMS#3ZZTRPBF; LCSC C514444
U502: TPS1H200AQDGNRQ1; SOP65P490X110-9N; Manufacturer Part Numbn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 TPS1H200AQDGNRQ1; LCSC C2653785
U503: Buffer_74LVC1G125DRYR; DRY6; Manufacturer Part Number SN74LVC1G125DRYR; LCSC C527546

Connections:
/+3.3V: C501.1, C504.1, R505.1, R506.1, U501.6 (VDDS), U503.6 (VCC); also elsewhere on the board
/+5V: C502.1, U501.7 (POL), U501.8 (PHA), U501.9 (VDD), U501.12 (MSTR); also elsewhere on the board
/GND: C501.2, C502.2, C503.2, C504.2, J501.A1 (GND), J501.A12 (GND), J501.B1 (GND), J501.B12 (GND), J501.S1 (SHIELD), J501.S2 (SHIELD), R504.2, U501.13 (SLOW), U501.14 (GND), U502.2 (DIAG_EN), U502.4 (CL), U502.5 (DELAY), U502.6 (GND), U502.9 (EP), U503.3 (GND); also elsewhere on the board
/PRISM_CIPO: U503.4; also elsewhere on the board
/PRISM_COPI: U501.2 (MOSI); also elsewhere on the board
/PRISM_SCK: U501.4 (SCK); also elsewhere on the board
/VAA: U502.8 (VS); also elsewhere on the board
/prism-0/CIPO_UNBUFFERED: R505.2, U501.3 (MISO), U503.2
/prism-0/CT: C503.1, TR501.6 (TCT)
/prism-0/I0+: J501.A6 (D+), J501.B6 (D+), TR501.5 (MX+)
/prism-0/I0-: J501.A7 (D-), J501.B7 (D-), TR501.4 (MX-)
/prism-0/I1+: FL501.4, TR501.1 (TD+)
/prism-0/I1-: FL501.3, TR501.2 (TD-)
/prism-0/I2+: FL501.1, R501.1, U501.11 (IP)
/prism-0/I2-: FL501.2, R501.2, U501.10 (IM)
/prism-0/IBIAS: R503.1, U501.16 (IBIAS)
/prism-0/ICMP: R503.2, R504.1, U501.15 (ICMP)
/prism-0/VBB: D501.2 (A), U502.7 (OUT)
/prism-0/VCC: D501.1 (K), J501.A4 (VBUS), J501.A9 (VBUS), J501.B4 (VBUS), J501.B9 (VBUS)
/~PRISMS_RESET: R502.1, U501.1 (EN); also elsewhere on the board
/~PRISM_CS_0: R506.2, U501.5 (~CS), U503.1 (~OE); also elsewhere on the board
unnamed: R502.2, U502.1 (IN)

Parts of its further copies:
C601, C602, C604, C701, C702, C704, C801, C802, C804, C901, C902, C904, C1001, C1002, C1004, C1101, C1102, C1104: 0.1uF_100V; C_0402_1005Metric; Manufacturer Part Number GRM155R62A104KE14D; LCSC C162178
C603, C703, C803, C903, C1003, C1103: 27pF_50V; C_0402_1005Metric; Manufacturer Part Number 0402CG270J500NT; LCSC C1557
D601, D701, D801, D901, D1001, D1101: D_SCHOTTKY_20V_1A; SOD-123FL; Manufacturer Part Number DSK36; LCSC C106913
FL601, FL701, FL801, FL901, FL1001, FL1101: Choke_CMF_ACT45B-220-2P; SMD_0-2P-TL003_TDK-L; Manufacturer Part Number ACT45B-220-2P-TL003; LCSC C88055
J601, J701, J801, J901, J1001, J1101: Connector_USB_C_Receptacle_USB2.0_16P_GT-USB-7047C; USB_C_Receptacle_GT-USB-7047C_16P_TopMnt_Horizontal; Manufacturer Part Number GT-USB-7047C; LCSC C963218
R601, R701, R801, R901, R1001, R1101: 100; R_0402_1005Metric; Manufacturer Part Number 0402WGF1000TCE; LCSC C25076
R602, R702, R802, R902, R1002, R1102: 4.7k; R_0402_1005Metric; Manufacturer Part Number 0402WGF4701TCE; LCSC C25900
R603, R703, R803, R903, R1003, R1103: 1.4k; R_0402_1005Metric; Manufacturer Part Number RC0402FR-071K4L; LCSC C375491
R604, R704, R804, R904, R1004, R1104: 604; R_0402_1005Metric; Manufacturer Part Number ERJ2RKF6040X; LCSC C2076855
R605, R606, R705, R706, R805, R806, R905, R906, R1005, R1006, R1105, R1106: 1.8k; R_0402_1005Metric; Manufacturer Part Number ERJ2GEJ182X; LCSC C409855
TR601, TR701, TR801, TR901, TR1001, TR1101: 1:1; FB020G00; Manufacturer Part Number FB020G00; LCSC C19673866
U601, U701, U801, U901, U1001, U1101: LTC6820HMS-TRPBF; MS_05-08-1669_ADI; Manufacturer Part Number LTC6820HMS#3ZZTRPBF; LCSC C514444
U602, U702, U802, U902, U1002, U1102: TPS1H200AQDGNRQ1; SOP65P490X110-9N; Manufacturer Part Numbn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 TPS1H200AQDGNRQ1; LCSC C2653785
U603, U703, U803, U903, U1003, U1103: Buffer_74LVC1G125DRYR; DRY6; Manufacturer Part Number SN74LVC1G125DRYR; LCSC C527546

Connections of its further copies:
/+3.3V: C601.1, C604.1, C701.1, C704.1, C801.1, C804.1, C901.1, C904.1, C1001.1, C1004.1, C1101.1, C1104.1, R605.1, R606.1, R705.1, R706.1, R805.1, R806.1, R905.1, R906.1, R1005.1, R1006.1, R1105.1, R1106.1, U601.6 (VDDS), U603.6 (VCC), U701.6 (VDDS), U703.6 (VCC), U801.6 (VDDS), U803.6 (VCC), U901.6 (VDDS), U903.6 (VCC), U1001.6 (VDDS), U1003.6 (VCC), U1101.6 (VDDS), U1103.6 (VCC); also elsewhere on the board
/+5V: C602.1, C702.1, C802.1, C902.1, C1002.1, C1102.1, U601.7 (POL), U601.8 (PHA), U601.9 (VDD), U601.12 (MSTR), U701.7 (POL), U701.8 (PHA), U701.9 (VDD), U701.12 (MSTR), U801.7 (POL), U801.8 (PHA), U801.9 (VDD), U801.12 (MSTR), U901.7 (POL), U901.8 (PHA), U901.9 (VDD), U901.12 (MSTR), U1001.7 (POL), U1001.8 (PHA), U1001.9 (VDD), U1001.12 (MSTR), U1101.7 (POL), U1101.8 (PHA), U1101.9 (VDD), U1101.12 (MSTR); also elsewhere on the board
/GND: C601.2, C602.2, C603.2, C604.2, C701.2, C702.2, C703.2, C704.2, C801.2, C802.2, C803.2, C804.2, C901.2, C902.2, C903.2, C904.2, C1001.2, C1002.2, C1003.2, C1004.2, C1101.2, C1102.2, C1103.2, C1104.2, J601.A1 (GND), J601.A12 (GND), J601.B1 (GND), J601.B12 (GND), J601.S1 (SHIELD), J601.S2 (SHIELD), J701.A1 (GND), J701.A12 (GND), J701.B1 (GND), J701.B12 (GND), J701.S1 (SHIELD), J701.S2 (SHIELD), J801.A1 (GND), J801.A12 (GND), J801.B1 (GND), J801.B12 (GND), J801.S1 (SHIELD), J801.S2 (SHIELD), J901.A1 (GND), J901.A12 (GND), J901.B1 (GND), J901.B12 (GND), J901.S1 (SHIELD), J901.S2 (SHIELD), J1001.A1 (GND), J1001.A12 (GND), J1001.B1 (GND), J1001.B12 (GND), J1001.S1 (SHIELD), J1001.S2 (SHIELD), J1101.A1 (GND), J1101.A12 (GND), J1101.B1 (GND), J1101.B12 (GND), J1101.S1 (SHIELD), J1101.S2 (SHIELD), R604.2, R704.2, R804.2, R904.2, R1004.2, R1104.2, U601.13 (SLOW), U601.14 (GND), U602.2 (DIAG_EN), U602.4 (CL), U602.5 (DELAY), U602.6 (GND), U602.9 (EP), U603.3 (GND), U701.13 (SLOW), U701.14 (GND), U702.2 (DIAG_EN), U702.4 (CL), U702.5 (DELAY), U702.6 (GND), U702.9 (EP), U703.3 (GND), U801.13 (SLOW), U801.14 (GND), U802.2 (DIAG_EN), U802.4 (CL), U802.5 (DELAY), U802.6 (GND), U802.9 (EP), U803.3 (GND), U901.13 (SLOW), U901.14 (GND), U902.2 (DIAG_EN), U902.4 (CL), U902.5 (DELAY), U902.6 (GND), U902.9 (EP), U903.3 (GND), U1001.13 (SLOW), U1001.14 (GND), U1002.2 (DIAG_EN), U1002.4 (CL), U1002.5 (DELAY), U1002.6 (GND), U1002.9 (EP), U1003.3 (GND), U1101.13 (SLOW), U1101.14 (GND), U1102.2 (DIAG_EN), U1102.4 (CL), U1102.5 (DELAY), U1102.6 (GND), U1102.9 (EP), U1103.3 (GND); also elsewhere on the board
/PRISM_CIPO: U603.4, U703.4, U803.4, U903.4, U1003.4, U1103.4; also elsewhere on the board
/PRISM_COPI: U601.2 (MOSI), U701.2 (MOSI), U801.2 (MOSI), U901.2 (MOSI), U1001.2 (MOSI), U1101.2 (MOSI); also elsewhere on the board
/PRISM_SCK: U601.4 (SCK), U701.4 (SCK), U801.4 (SCK), U901.4 (SCK), U1001.4 (SCK), U1101.4 (SCK); also elsewhere on the board
/VAA: U602.8 (VS), U702.8 (VS), U802.8 (VS), U902.8 (VS), U1002.8 (VS), U1102.8 (VS); also elsewhere on the board
/prism-1/CIPO_UNBUFFERED: R605.2, U601.3 (MISO), U603.2
/prism-1/CT: C603.1, TR601.6 (TCT)
/prism-1/I0+: J601.A6 (D+), J601.B6 (D+), TR601.5 (MX+)
/prism-1/I0-: J601.A7 (D-), J601.B7 (D-), TR601.4 (MX-)
/prism-1/I1+: FL601.4, TR601.1 (TD+)
/prism-1/I1-: FL601.3, TR601.2 (TD-)
/prism-1/I2+: FL601.1, R601.1, U601.11 (IP)
/prism-1/I2-: FL601.2, R601.2, U601.10 (IM)
/prism-1/IBIAS: R603.1, U601.16 (IBIAS)
/prism-1/ICMP: R603.2, R604.1, U601.15 (ICMP)
/prism-1/VBB: D601.2 (A), U602.7 (OUT)
/prism-1/VCC: D601.1 (K), J601.A4 (VBUS), J601.A9 (VBUS), J601.B4 (VBUS), J601.B9 (VBUS)
/prism-2/CIPO_UNBUFFERED: R705.2, U701.3 (MISO), U703.2
/prism-2/CT: C703.1, TR701.6 (TCT)
/prism-2/I0+: J701.A6 (D+), J701.B6 (D+), TR701.5 (MX+)
/prism-2/I0-: J701.A7 (D-), J701.B7 (D-), TR701.4 (MX-)
/prism-2/I1+: FL701.4, TR701.1 (TD+)
/prism-2/I1-: FL701.3, TR701.2 (TD-)
/prism-2/I2+: FL701.1, R701.1, U701.11 (IP)
/prism-2/I2-: FL701.2, R701.2, U701.10 (IM)
/prism-2/IBIAS: R703.1, U701.16 (IBIAS)
/prism-2/ICMP: R703.2, R704.1, U701.15 (ICMP)
/prism-2/VBB: D701.2 (A), U702.7 (OUT)
/prism-2/VCC: D701.1 (K), J701.A4 (VBUS), J701.A9 (VBUS), J701.B4 (VBUS), J701.B9 (VBUS)
/prism-3/CIPO_UNBUFFERED: R805.2, U801.3 (MISO), U803.2
/prism-3/CT: C803.1, TR801.6 (TCT)
/prism-3/I0+: J801.A6 (D+), J801.B6 (D+), TR801.5 (MX+)
/prism-3/I0-: J801.A7 (D-), J801.B7 (D-), TR801.4 (MX-)
/prism-3/I1+: FL801.4, TR801.1 (TD+)
/prism-3/I1-: FL801.3, TR801.2 (TD-)
/prism-3/I2+: FL801.1, R801.1, U801.11 (IP)
/prism-3/I2-: FL801.2, R801.2, U801.10 (IM)
/prism-3/IBIAS: R803.1, U801.16 (IBIAS)
/prism-3/ICMP: R803.2, R804.1, U801.15 (ICMP)
/prism-3/VBB: D801.2 (A), U802.7 (OUT)
/prism-3/VCC: D801.1 (K), J801.A4 (VBUS), J801.A9 (VBUS), J801.B4 (VBUS), J801.B9 (VBUS)
/prism-4/CIPO_UNBUFFERED: R1005.2, U1001.3 (MISO), U1003.2
/prism-4/CT: C1003.1, TR1001.6 (TCT)
/prism-4/I0+: J1001.A6 (D+), J1001.B6 (D+), TR1001.5 (MX+)
/prism-4/I0-: J1001.A7 (D-), J1001.B7 (D-), TR1001.4 (MX-)
/prism-4/I1+: FL1001.4, TR1001.1 (TD+)
/prism-4/I1-: FL1001.3, TR1001.2 (TD-)
/prism-4/I2+: FL1001.1, R1001.1, U1001.11 (IP)
/prism-4/I2-: FL1001.2, R1001.2, U1001.10 (IM)
/prism-4/IBIAS: R1003.1, U1001.16 (IBIAS)
/prism-4/ICMP: R1003.2, R1004.1, U1001.15 (ICMP)
/prism-4/VBB: D1001.2 (A), U1002.7 (OUT)
/prism-4/VCC: D1001.1 (K), J1001.A4 (VBUS), J1001.A9 (VBUS), J1001.B4 (VBUS), J1001.B9 (VBUS)
/prism-5/CIPO_UNBUFFERED: R905.2, U901.3 (MISO), U903.2
/prism-5/CT: C903.1, TR901.6 (TCT)
/prism-5/I0+: J901.A6 (D+), J901.B6 (D+), TR901.5 (MX+)
/prism-5/I0-: J901.A7 (D-), J901.B7 (D-), TR901.4 (MX-)
/prism-5/I1+: FL901.4, TR901.1 (TD+)
/prism-5/I1-: FL901.3, TR901.2 (TD-)
/prism-5/I2+: FL901.1, R901.1, U901.11 (IP)
/prism-5/I2-: FL901.2, R901.2, U901.10 (IM)
/prism-5/IBIAS: R903.1, U901.16 (IBIAS)
/prism-5/ICMP: R903.2, R904.1, U901.15 (ICMP)
/prism-5/VBB: D901.2 (A), U902.7 (OUT)
/prism-5/VCC: D901.1 (K), J901.A4 (VBUS), J901.A9 (VBUS), J901.B4 (VBUS), J901.B9 (VBUS)
/prism-6/CIPO_UNBUFFERED: R1105.2, U1101.3 (MISO), U1103.2
/prism-6/CT: C1103.1, TR1101.6 (TCT)
/prism-6/I0+: J1101.A6 (D+), J1101.B6 (D+), TR1101.5 (MX+)
/prism-6/I0-: J1101.A7 (D-), J1101.B7 (D-), TR1101.4 (MX-)
/prism-6/I1+: FL1101.4, TR1101.1 (TD+)
/prism-6/I1-: FL1101.3, TR1101.2 (TD-)
/prism-6/I2+: FL1101.1, R1101.1, U1101.11 (IP)
/prism-6/I2-: FL1101.2, R1101.2, U1101.10 (IM)
/prism-6/IBIAS: R1103.1, U1101.16 (IBIAS)
/prism-6/ICMP: R1103.2, R1104.1, U1101.15 (ICMP)
/prism-6/VBB: D1101.2 (A), U1102.7 (OUT)
/prism-6/VCC: D1101.1 (K), J1101.A4 (VBUS), J1101.A9 (VBUS), J1101.B4 (VBUS), J1101.B9 (VBUS)
/~PRISMS_RESET: R602.1, R702.1, R802.1, R902.1, R1002.1, R1102.1, U601.1 (EN), U701.1 (EN), U801.1 (EN), U901.1 (EN), U1001.1 (EN), U1101.1 (EN); also elsewhere on the board
/~PRISM_CS_1: R606.2, U601.5 (~CS), U603.1 (~OE); also elsewhere on the board
/~PRISM_CS_2: R706.2, U701.5 (~CS), U703.1 (~OE); also elsewhere on the board
/~PRISM_CS_3: R806.2, U801.5 (~CS), U803.1 (~OE); also elsewhere on the board
/~PRISM_CS_4: R1006.2, U1001.5 (~CS), U1003.1 (~OE); also elsewhere on the board
/~PRISM_CS_5: R906.2, U901.5 (~CS), U903.1 (~OE); also elsewhere on the board
/~PRISM_CS_6: R1106.2, U1101.5 (~CS), U1103.1 (~OE); also elsewhere on the board
unnamed: R602.2, U602.1 (IN)
unnamed: R702.2, U702.1 (IN)
unnamed: R802.2, U802.1 (IN)
unnamed: R902.2, U902.1 (IN)
unnamed: R1002.2, U1002.1 (IN)
unnamed: R1102.2, U1102.1 (IN)

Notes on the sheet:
RB1
RB2
USB C Cable Differential Impedance 90 Ohm
SPI MODE 3
FAST MODE

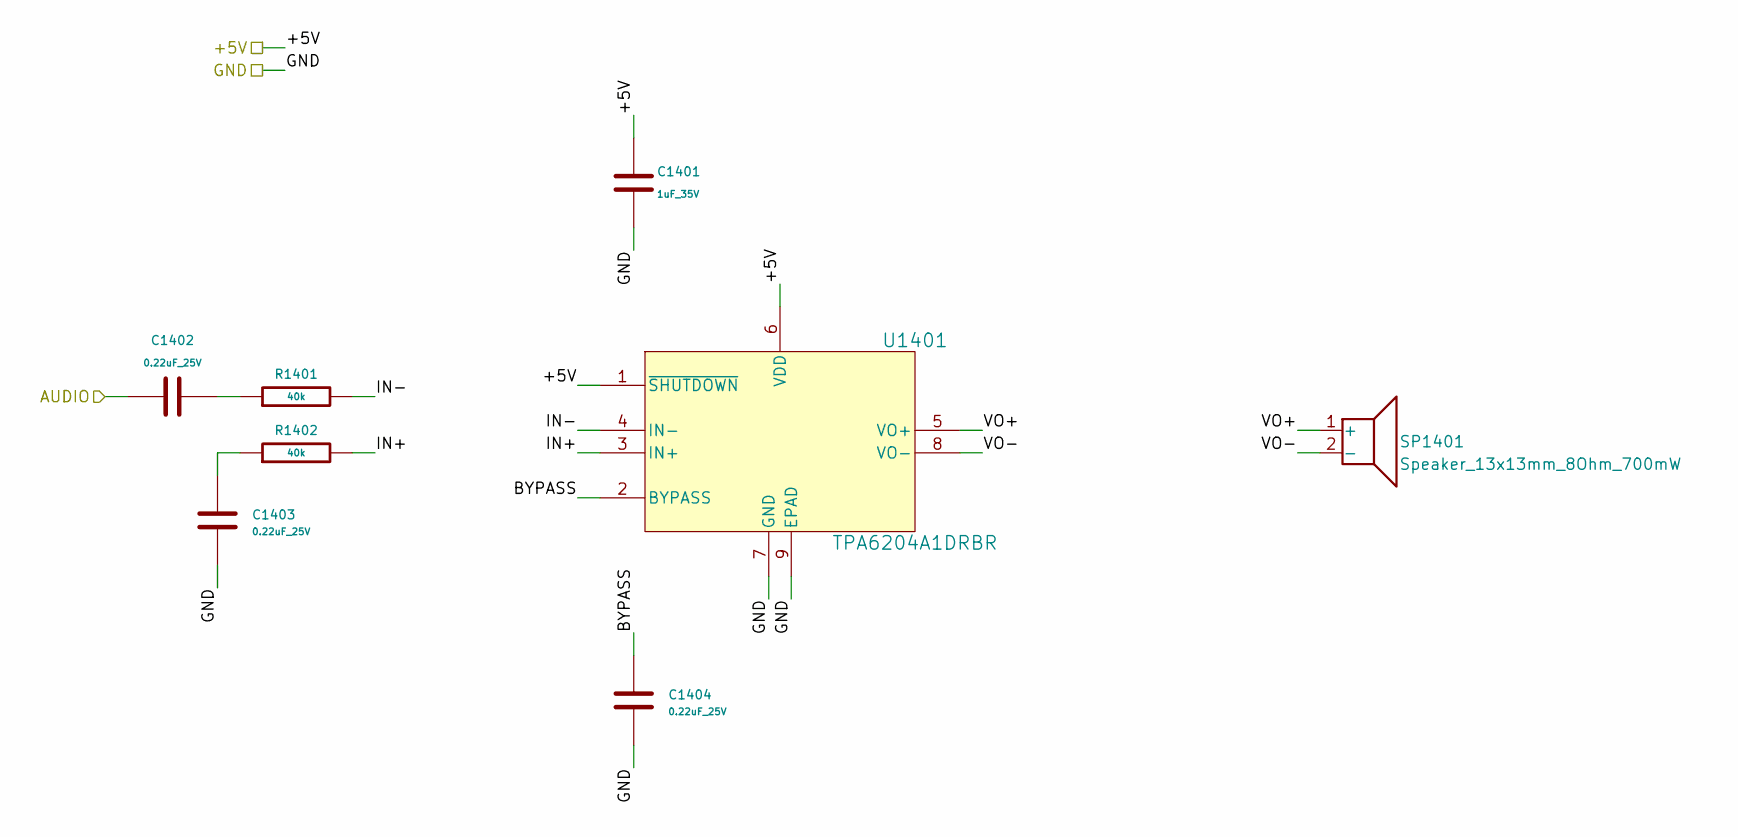
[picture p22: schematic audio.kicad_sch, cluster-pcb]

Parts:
C1401: 1uF_35V; C_0402_1005Metric; Manufacturer Part Number CL05A105KL5NRNC; LCSC C307413
C1402, C1403, C1404: 0.22uF_25V; C_0402_1005Metric; Manufacturer Part Number GRT155C81E224KE01D; LCSC C126623
R1401, R1402: 40k; R_0603_1608Metric; Manufacturer Part Number SCR0603F40K; LCSC C3016445
SP1401: Speaker_13x13mm_8Ohm_700mW; Speaker_13x13mm_KLJ-01304T-08R07W; Manufacturer Part Number KLJ-01304T-08R07W; LCSC C18186315
U1401: TPA6204A1DRBR; DRB8_1P75X1P5; Manufacturer Part Number TPA6204A1DRBR; LCSC C12400

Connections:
/+5V: C1401.1, U1401.1 (~SHUTDOWN), U1401.6 (VDD); also elsewhere on the board
/AUDIO: C1402.1; also elsewhere on the board
/GND: C1401.2, C1403.1, C1404.1, U1401.7 (GND), U1401.9 (EPAD); also elsewhere on the board
/audio/BYPASS: C1404.2, U1401.2 (BYPASS)
/audio/IN+: R1402.2, U1401.3 (IN+)
/audio/IN-: R1401.2, U1401.4 (IN-)
/audio/VO+: SP1401.1 (+), U1401.5 (VO+)
/audio/VO-: SP1401.2 (-), U1401.8 (VO-)
unnamed: C1402.2, R1401.1
unnamed: C1403.2, R1402.1

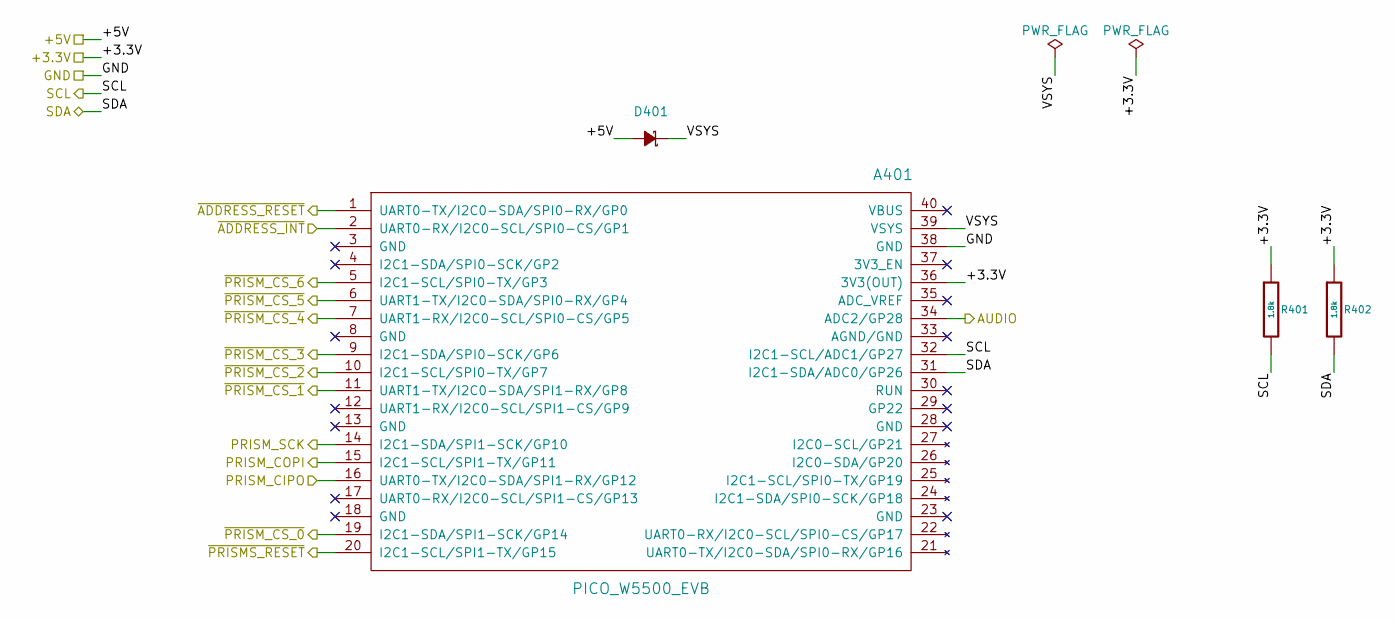
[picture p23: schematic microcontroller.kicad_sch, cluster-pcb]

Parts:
A401: PICO_W5500_EVB; Pico-W5500-EVB_Header_Holes
D401: D_SCHOTTKY_20V_1A; SOD-123FL; Manufacturer Part Number MBR120VLSFT1G; LCSC C223608
R401, R402: 1.8k; R_0402_1005Metric; Manufacturer Part Number ERJ2GEJ182X; LCSC C409855

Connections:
/+3.3V: A401.36 (3V3(OUT)), R401.1, R402.1; also elsewhere on the board
/+5V: D401.2 (A); also elsewhere on the board
/AUDIO: A401.34 (ADC2/GP28); also elsewhere on the board
/GND: A401.38 (GND); also elsewhere on the board
/PRISM_CIPO: A401.16 (UART0-TX/I2C0-SDA/SPI1-RX/GP12); also elsewhere on the board
/PRISM_COPI: A401.15 (I2C1-SCL/SPI1-TX/GP11); also elsewhere on the board
/PRISM_SCK: A401.14 (I2C1-SDA/SPI1-SCK/GP10); also elsewhere on the board
/SCL: A401.32 (I2C1-SCL/ADC1/GP27), R401.2; also elsewhere on the board
/SDA: A401.31 (I2C1-SDA/ADC0/GP26), R402.2; also elsewhere on the board
/microcontroller/VSYS: A401.39 (VSYS), D401.1 (K)
/~ADDRESS_INT: A401.2 (UART0-RX/I2C0-SCL/SPI0-CS/GP1); also elsewhere on the board
/~ADDRESS_RESET: A401.1 (UART0-TX/I2C0-SDA/SPI0-RX/GP0); also elsewhere on the board
/~PRISMS_RESET: A401.20 (I2C1-SCL/SPI1-TX/GP15); also elsewhere on the board
/~PRISM_CS_0: A401.19 (I2C1-SDA/SPI1-SCK/GP14); also elsewhere on the board
/~PRISM_CS_1: A401.11 (UART1-TX/I2C0-SDA/SPI1-RX/GP8); also elsewhere on the board
/~PRISM_CS_2: A401.10 (I2C1-SCL/SPI0-TX/GP7); also elsewhere on the board
/~PRISM_CS_3: A401.9 (I2C1-SDA/SPI0-SCK/GP6); also elsewhere on the board
/~PRISM_CS_4: A401.7 (UART1-RX/I2C0-SCL/SPI0-CS/GP5); also elsewhere on the board
/~PRISM_CS_5: A401.6 (UART1-TX/I2C0-SDA/SPI0-RX/GP4); also elsewhere on the board
/~PRISM_CS_6: A401.5 (I2C1-SCL/SPI0-TX/GP3); also elsewhere on the board

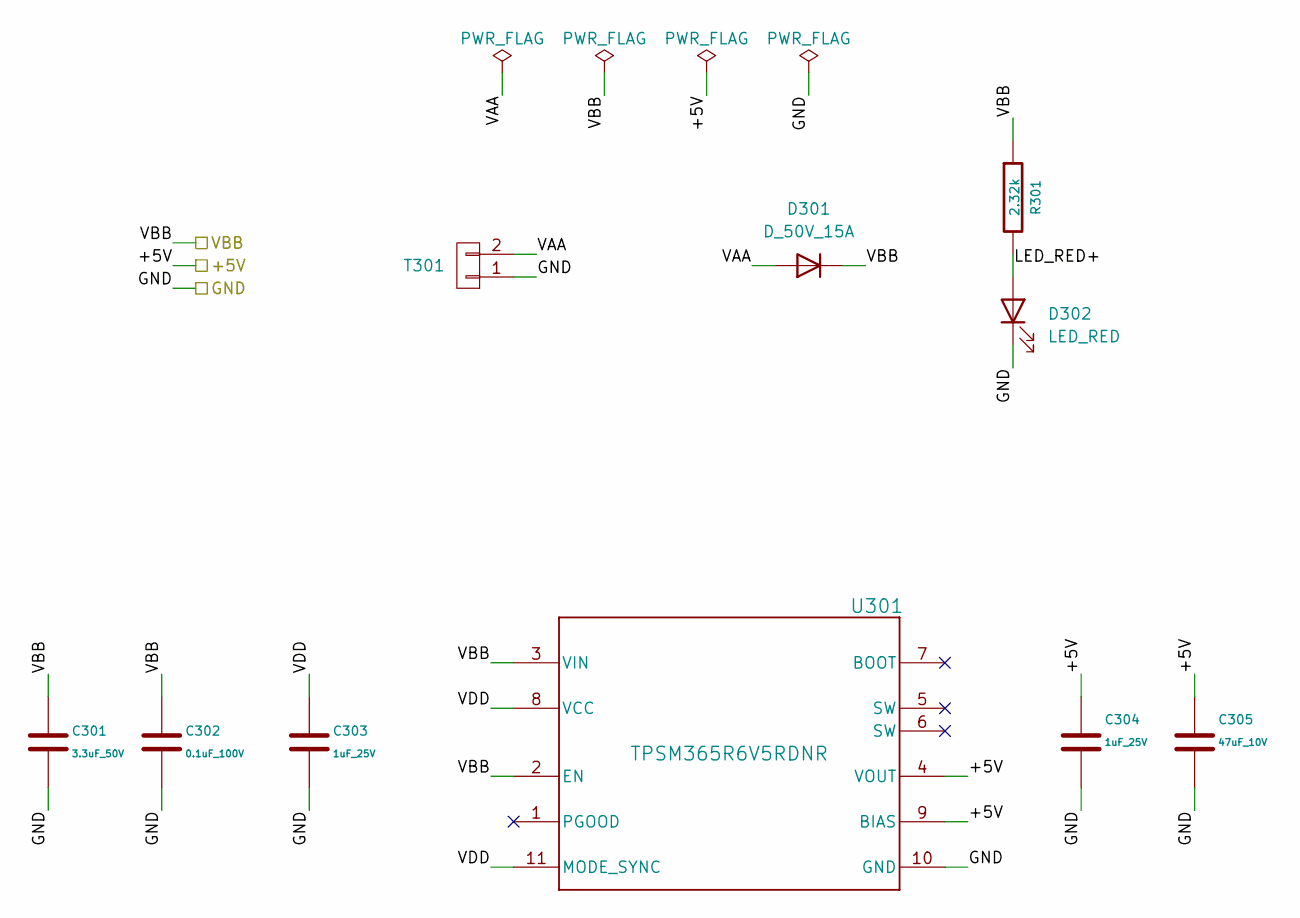
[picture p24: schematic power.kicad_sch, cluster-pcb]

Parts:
C301: 3.3uF_50V; C_1210_3225Metric; Manufacturer Part Number FS32X335K500EGG; LCSC C1021610
C302: 0.1uF_100V; C_0402_1005Metric; Manufacturer Part Number GRM155R62A104KE14D; LCSC C162178
C303, C304: 1uF_25V; C_0402_1005Metric; Manufacturer Part Number GRT155R61E105KE01D; LCSC C711085
C305: 47uF_10V; C_0805_2012Metric; Manufacturer Part Number CGA0805X5R476M100MT; LCSC C6119904
D301: D_50V_15A; POWERDI5_DIO; Manufacturer Part Number SBRT15U50SP5-13; LCSC C211388
D302: LED_RED; LED_0402-1005_KNB; Manufacturer Part Number APHHS1005SURCK; LCSC C2852592
R301: 2.32k; R_0805_2012Metric; Manufacturer Part Number RA73F2A2K32BTD; LCSC C3961061
T301: TERM_BLK_HDR_2POS_90DEG_0.2IN; PHOENIX_1757242; Manufacturer Part Number 1757242; LCSC C90074
U301: TPSM365R6V5RDNR; RDN0011A-MFG; Manufacturer Part Number TPSM365R6V5RDNR; LCSC C19078014

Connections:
/+5V: C304.1, C305.1, U301.4 (VOUT), U301.9 (BIAS); also elsewhere on the board
/GND: C301.2, C302.2, C303.2, C304.2, C305.2, D302.1 (K), T301.1, U301.10 (GND); also elsewhere on the board
/VAA: C301.1, C302.1, D301.1 (K), R301.1, U301.2 (EN), U301.3 (VIN); also elsewhere on the board
/power/LED_RED+: D302.2 (A), R301.2
/power/VAA: D301.2 (A), T301.2
/power/VDD: C303.1, U301.8 (VCC), U301.11 (MODE_SYNC)

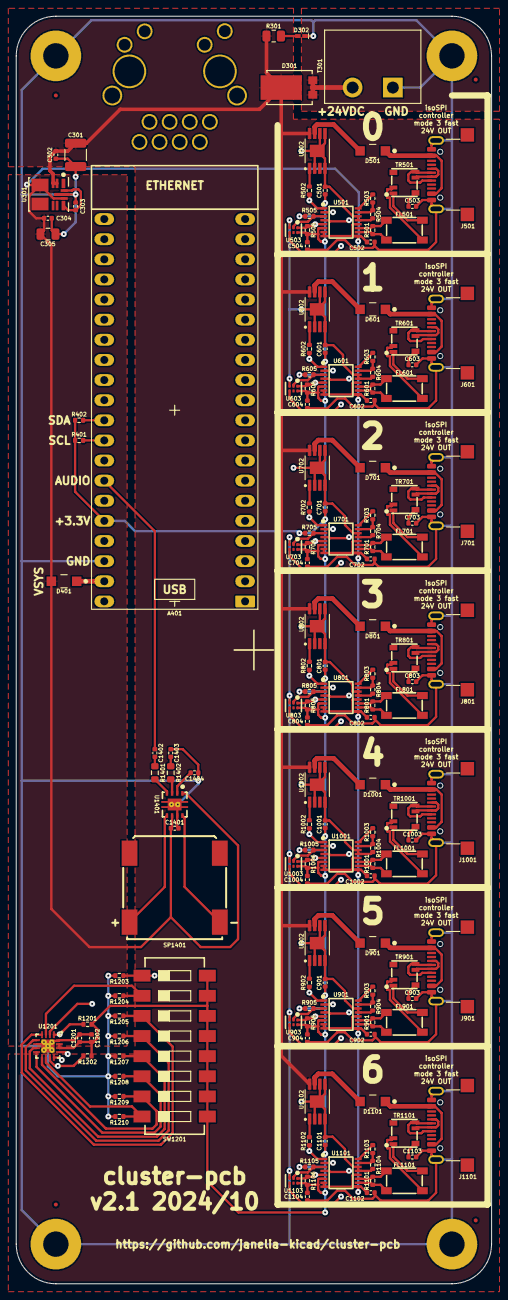
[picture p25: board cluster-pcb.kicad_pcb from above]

Board: 4 copper layers, 60.0 x 160.0 mm, 163 parts (0 on the bottom side), 130 nets.

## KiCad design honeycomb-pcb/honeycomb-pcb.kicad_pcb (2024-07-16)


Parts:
FID201, FID202, FID203, FID204: FIDUCIAL_0.5mm_MASK1mm; FIDUCIAL_0.5mm_Mask1mm
H201, H202, H203, H204: MountingHole_M3_Pad; MountingHole_3.2mm_M3_Pad

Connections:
/GND: H201.1, H202.1, H203.1, H204.1; also elsewhere on the board

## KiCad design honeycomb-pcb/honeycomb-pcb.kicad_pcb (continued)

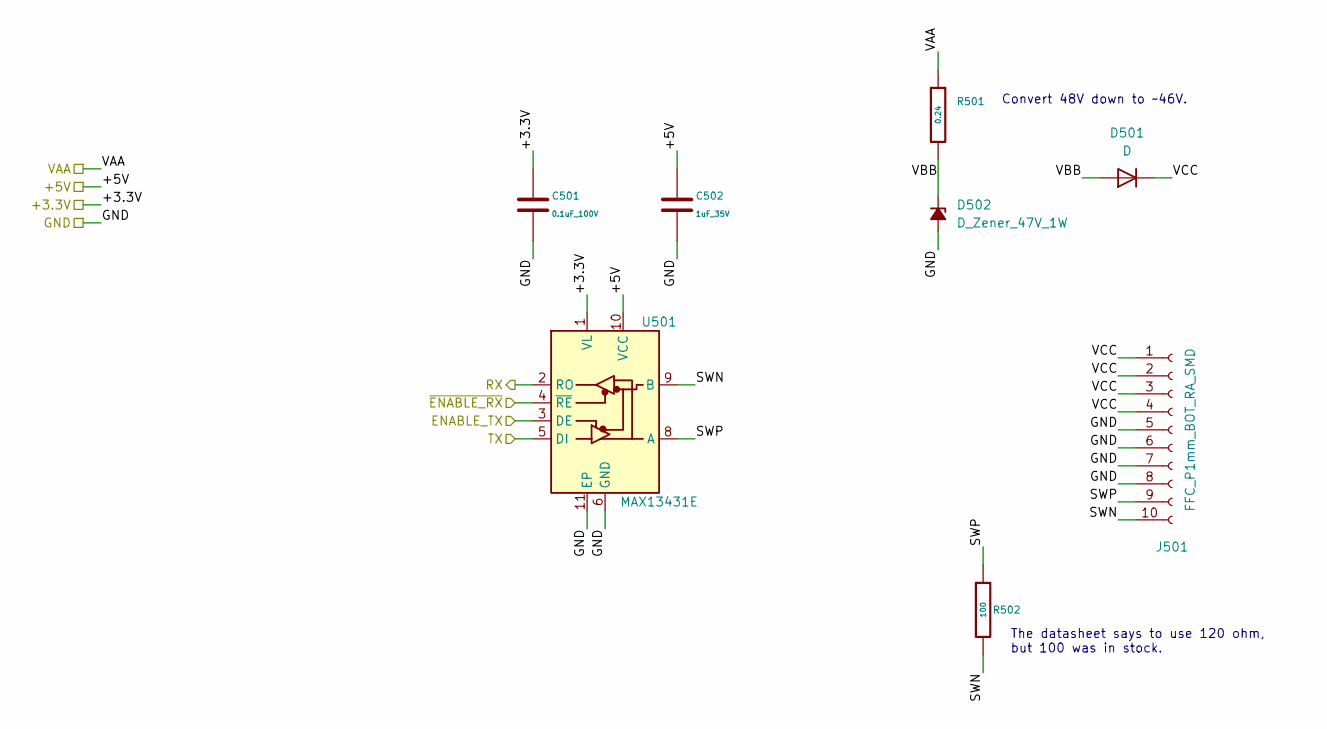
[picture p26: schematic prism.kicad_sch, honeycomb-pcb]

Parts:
C501: 0.1uF_100V; C_0402_1005Metric; Manufacturer Part Number GRM155R62A104KE14D; LCSC C162178
C502: 1uF_35V; C_0402_1005Metric; Manufacturer Part Number CL05A105KL5NRNC; LCSC C307413
D501: D; D_SMB; Manufacturer Part Number ES2G; LCSC C4944961
D502: D_Zener_47V_1W; D_SMA; Manufacturer Part Number 1SMAF4756A; LCSC C475448
J501: FFC_P1mm_BOT_RA_SMD; CONN_C2914097; Manufacturer Part Number 1.0K-FX-10PWBG; LCSC C2914097
R501: 0.24; R_2512_6332Metric; Manufacturer Part Number FRL2512JR240TS; LCSC C2960776
R502: 100; R_0402_1005Metric; Manufacturer Part Number 0402WGF1000TCE; LCSC C25076
U501: MAX13431E; 21-0137I_T1033-1_MXM; Manufacturer Part Number MAX13431EETB+T; LCSC C2672811

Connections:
/+3.3V: C501.1, U501.1 (VL); also elsewhere on the board
/+5V: C502.1, U501.10 (VCC); also elsewhere on the board
/ENABLE_TX_0: U501.3 (DE); also elsewhere on the board
/GND: C501.2, C502.2, D502.2 (A), J501.5, J501.6, J501.7, J501.8, U501.6 (GND), U501.11 (EP); also elsewhere on the board
/RX: U501.2 (RO); also elsewhere on the board
/TX: U501.5 (DI); also elsewhere on the board
/VCC: R501.1; also elsewhere on the board
/prism0/SWN: J501.10, R502.2, U501.9 (B)
/prism0/SWP: J501.9, R502.1, U501.8 (A)
/prism0/VBB: D501.2 (A), D502.1 (K), R501.2
/prism0/VCC: D501.1 (K), J501.1, J501.2, J501.3, J501.4
/~ENABLE_RX_0: U501.4 (~RE); also elsewhere on the board

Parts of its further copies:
C601, C701, C801, C901, C1001, C1101: 0.1uF_100V; C_0402_1005Metric; Manufacturer Part Number GRM155R62A104KE14D; LCSC C162178
C602, C702, C802, C902, C1002, C1102: 1uF_35V; C_0402_1005Metric; Manufacturer Part Number CL05A105KL5NRNC; LCSC C307413
D601, D701, D801, D901, D1001, D1101: D; D_SMB; Manufacturer Part Number ES2G; LCSC C4944961
D602, D702, D802, D902, D1002, D1102: D_Zener_47V_1W; D_SMA; Manufacturer Part Number 1SMAF4756A; LCSC C475448
J601, J701, J801, J901, J1001, J1101: FFC_P1mm_BOT_RA_SMD; CONN_C2914097; Manufacturer Part Number 1.0K-FX-10PWBG; LCSC C2914097
R601, R701, R801, R901, R1001, R1101: 0.24; R_2512_6332Metric; Manufacturer Part Number FRL2512JR240TS; LCSC C2960776
R602, R702, R802, R902, R1002, R1102: 100; R_0402_1005Metric; Manufacturer Part Number 0402WGF1000TCE; LCSC C25076
U601, U701, U801, U901, U1001, U1101: MAX13431E; 21-0137I_T1033-1_MXM; Manufacturer Part Number MAX13431EETB+T; LCSC C2672811

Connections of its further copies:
/+3.3V: C601.1, C701.1, C801.1, C901.1, C1001.1, C1101.1, U601.1 (VL), U701.1 (VL), U801.1 (VL), U901.1 (VL), U1001.1 (VL), U1101.1 (VL); also elsewhere on the board
/+5V: C602.1, C702.1, C802.1, C902.1, C1002.1, C1102.1, U601.10 (VCC), U701.10 (VCC), U801.10 (VCC), U901.10 (VCC), U1001.10 (VCC), U1101.10 (VCC); also elsewhere on the board
/ENABLE_TX_1: U601.3 (DE); also elsewhere on the board
/ENABLE_TX_2: U701.3 (DE); also elsewhere on the board
/ENABLE_TX_3: U801.3 (DE); also elsewhere on the board
/ENABLE_TX_4: U1001.3 (DE); also elsewhere on the board
/ENABLE_TX_5: U901.3 (DE); also elsewhere on the board
/ENABLE_TX_6: U1101.3 (DE); also elsewhere on the board
/GND: C601.2, C602.2, C701.2, C702.2, C801.2, C802.2, C901.2, C902.2, C1001.2, C1002.2, C1101.2, C1102.2, D602.2 (A), D702.2 (A), D802.2 (A), D902.2 (A), D1002.2 (A), D1102.2 (A), J601.5, J601.6, J601.7, J601.8, J701.5, J701.6, J701.7, J701.8, J801.5, J801.6, J801.7, J801.8, J901.5, J901.6, J901.7, J901.8, J1001.5, J1001.6, J1001.7, J1001.8, J1101.5, J1101.6, J1101.7, J1101.8, U601.6 (GND), U601.11 (EP), U701.6 (GND), U701.11 (EP), U801.6 (GND), U801.11 (EP), U901.6 (GND), U901.11 (EP), U1001.6 (GND), U1001.11 (EP), U1101.6 (GND), U1101.11 (EP); also elsewhere on the board
/RX: U601.2 (RO), U701.2 (RO), U801.2 (RO), U901.2 (RO), U1001.2 (RO), U1101.2 (RO); also elsewhere on the board
/TX: U601.5 (DI), U701.5 (DI), U801.5 (DI), U901.5 (DI), U1001.5 (DI), U1101.5 (DI); also elsewhere on the board
/VCC: R601.1, R701.1, R801.1, R901.1, R1001.1, R1101.1; also elsewhere on the board
/prism1/SWN: J601.10, R602.2, U601.9 (B)
/prism1/SWP: J601.9, R602.1, U601.8 (A)
/prism1/VBB: D601.2 (A), D602.1 (K), R601.2
/prism1/VCC: D601.1 (K), J601.1, J601.2, J601.3, J601.4
/prism2/SWN: J701.10, R702.2, U701.9 (B)
/prism2/SWP: J701.9, R702.1, U701.8 (A)
/prism2/VBB: D701.2 (A), D702.1 (K), R701.2
/prism2/VCC: D701.1 (K), J701.1, J701.2, J701.3, J701.4
/prism3/SWN: J801.10, R802.2, U801.9 (B)
/prism3/SWP: J801.9, R802.1, U801.8 (A)
/prism3/VBB: D801.2 (A), D802.1 (K), R801.2
/prism3/VCC: D801.1 (K), J801.1, J801.2, J801.3, J801.4
/prism4/SWN: J1001.10, R1002.2, U1001.9 (B)
/prism4/SWP: J1001.9, R1002.1, U1001.8 (A)
/prism4/VBB: D1001.2 (A), D1002.1 (K), R1001.2
/prism4/VCC: D1001.1 (K), J1001.1, J1001.2, J1001.3, J1001.4
/prism5/SWN: J901.10, R902.2, U901.9 (B)
/prism5/SWP: J901.9, R902.1, U901.8 (A)
/prism5/VBB: D901.2 (A), D902.1 (K), R901.2
/prism5/VCC: D901.1 (K), J901.1, J901.2, J901.3, J901.4
/prism6/SWN: J1101.10, R1102.2, U1101.9 (B)
/prism6/SWP: J1101.9, R1102.1, U1101.8 (A)
/prism6/VBB: D1101.2 (A), D1102.1 (K), R1101.2
/prism6/VCC: D1101.1 (K), J1101.1, J1101.2, J1101.3, J1101.4
/~ENABLE_RX_1: U601.4 (~RE); also elsewhere on the board
/~ENABLE_RX_2: U701.4 (~RE); also elsewhere on the board
/~ENABLE_RX_3: U801.4 (~RE); also elsewhere on the board
/~ENABLE_RX_4: U1001.4 (~RE); also elsewhere on the board
/~ENABLE_RX_5: U901.4 (~RE); also elsewhere on the board
/~ENABLE_RX_6: U1101.4 (~RE); also elsewhere on the board

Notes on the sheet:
The datasheet says to use 120 ohm, but 100 was in stock.
Convert 48V down to ~46V.

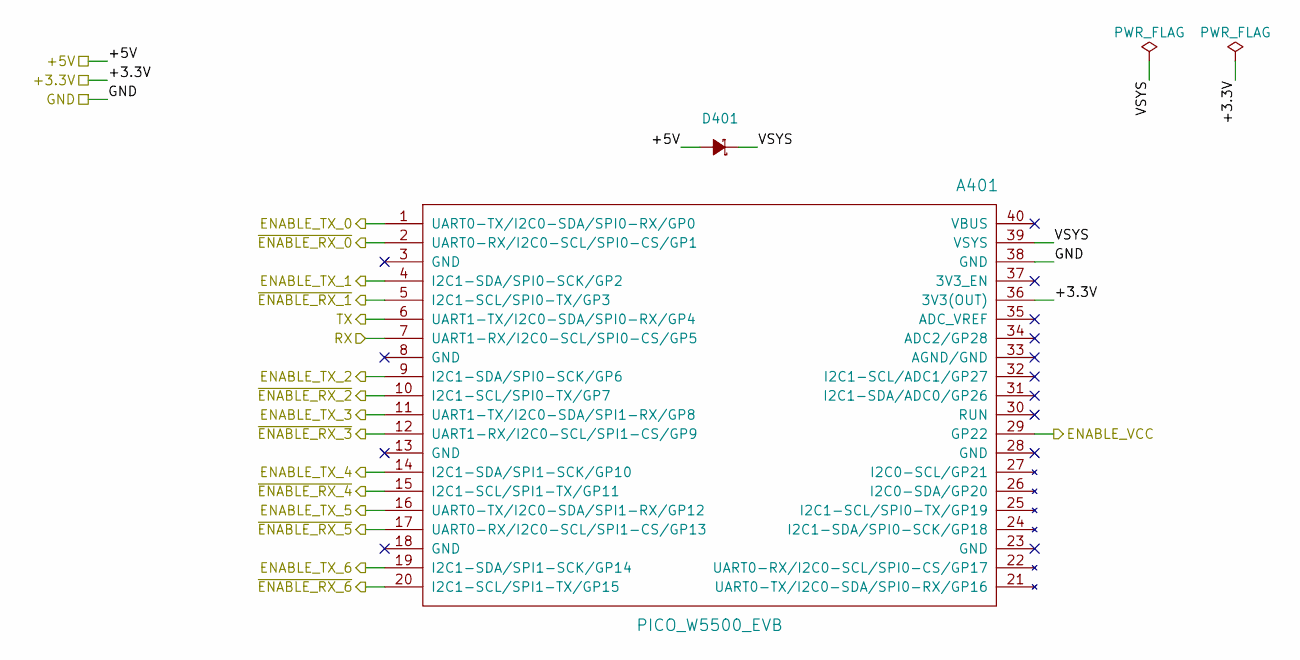
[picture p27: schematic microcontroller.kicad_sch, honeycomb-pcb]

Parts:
A401: PICO_W5500_EVB; Pico_Header_Holes
D401: D_SCHOTTKY_20V_1A; DIOM3616X98N; Manufacturer Part Number MBR120VLSFT1G; LCSC C223608

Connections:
/+3.3V: A401.36 (3V3(OUT)); also elsewhere on the board
/+5V: D401.2 (A); also elsewhere on the board
/ENABLE_TX_0: A401.1 (UART0-TX/I2C0-SDA/SPI0-RX/GP0); also elsewhere on the board
/ENABLE_TX_1: A401.4 (I2C1-SDA/SPI0-SCK/GP2); also elsewhere on the board
/ENABLE_TX_2: A401.9 (I2C1-SDA/SPI0-SCK/GP6); also elsewhere on the board
/ENABLE_TX_3: A401.11 (UART1-TX/I2C0-SDA/SPI1-RX/GP8); also elsewhere on the board
/ENABLE_TX_4: A401.14 (I2C1-SDA/SPI1-SCK/GP10); also elsewhere on the board
/ENABLE_TX_5: A401.16 (UART0-TX/I2C0-SDA/SPI1-RX/GP12); also elsewhere on the board
/ENABLE_TX_6: A401.19 (I2C1-SDA/SPI1-SCK/GP14); also elsewhere on the board
/ENABLE_VCC: A401.29 (GP22); also elsewhere on the board
/GND: A401.38 (GND); also elsewhere on the board
/RX: A401.7 (UART1-RX/I2C0-SCL/SPI0-CS/GP5); also elsewhere on the board
/TX: A401.6 (UART1-TX/I2C0-SDA/SPI0-RX/GP4); also elsewhere on the board
/microcontroller/VSYS: A401.39 (VSYS), D401.1 (K)
/~ENABLE_RX_0: A401.2 (UART0-RX/I2C0-SCL/SPI0-CS/GP1); also elsewhere on the board
/~ENABLE_RX_1: A401.5 (I2C1-SCL/SPI0-TX/GP3); also elsewhere on the board
/~ENABLE_RX_2: A401.10 (I2C1-SCL/SPI0-TX/GP7); also elsewhere on the board
/~ENABLE_RX_3: A401.12 (UART1-RX/I2C0-SCL/SPI1-CS/GP9); also elsewhere on the board
/~ENABLE_RX_4: A401.15 (I2C1-SCL/SPI1-TX/GP11); also elsewhere on the board
/~ENABLE_RX_5: A401.17 (UART0-RX/I2C0-SCL/SPI1-CS/GP13); also elsewhere on the board
/~ENABLE_RX_6: A401.20 (I2C1-SCL/SPI1-TX/GP15); also elsewhere on the board

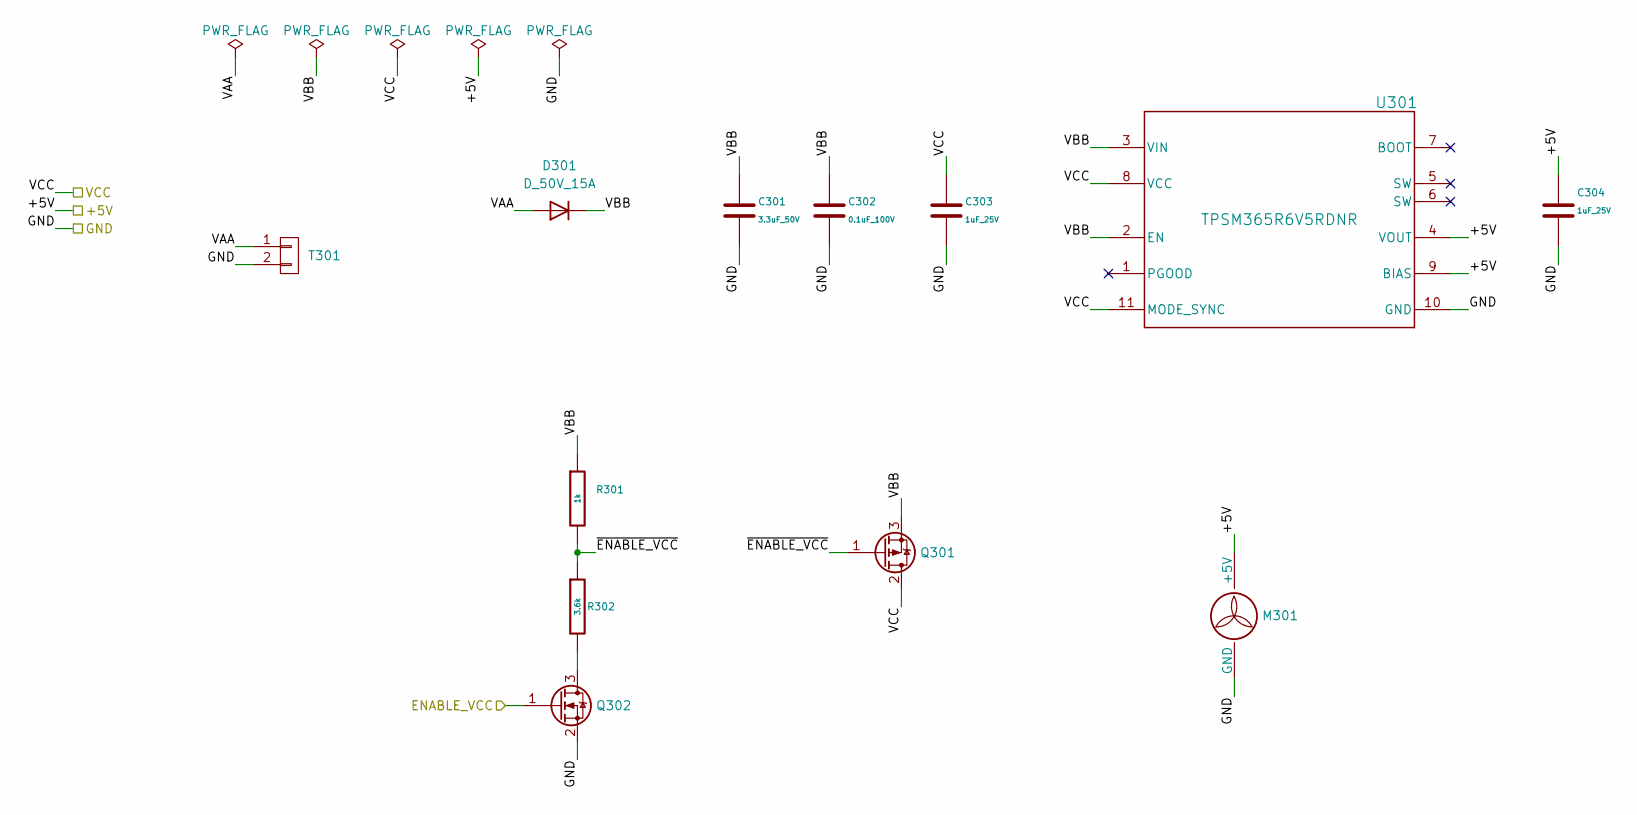
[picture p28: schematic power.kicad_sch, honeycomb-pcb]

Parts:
C301: 3.3uF_50V; C_1210_3225Metric; Manufacturer Part Number FS32X335K500EGG; LCSC C1021610
C302: 0.1uF_100V; C_0402_1005Metric; Manufacturer Part Number GRM155R62A104KE14D; LCSC C162178
C303, C304: 1uF_25V; C_0402_1005Metric; Manufacturer Part Number GRT155R61E105KE01D; LCSC C711085
D301: D_50V_15A; POWERDI5_DIO; Manufacturer Part Number SBRT15U50SP5-13; LCSC C211388
M301: Fan_5VDC_25x25x8mm; FAN_5VDC_25x25x8mm; Manufacturer Part Number 255M
Q301: MOSFET-P-CH-EN_60V_50A; TO-252-2; Manufacturer Part Number 30P06-VB; LCSC C709875
Q302: MOSFET-N-CH-EN_100V_260mA; SOT-23; Manufacturer Part Number 2SK1589-T1B-VB; LCSC C724949
R301: 1k; R_0402_1005Metric; Manufacturer Part Number RC0402FR-071KL; LCSC C106235
R302: 3.6k; R_0402_1005Metric; Manufacturer Part Number RM04JTN362; LCSC C162873
T301: TERM_BLK_HDR_2POS_90DEG_0.2IN; PHOENIX_1757242; Manufacturer Part Number 1757242; LCSC C90074
U301: TPSM365R6V5RDNR; RDN0011A-MFG; Manufacturer Part Number TPSM365R6V5RDNR; LCSC C19078014

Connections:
/+5V: C304.1, M301.1 (+5V), U301.4 (VOUT), U301.9 (BIAS); also elsewhere on the board
/ENABLE_VCC: Q302.1 (G); also elsewhere on the board
/GND: C301.2, C302.2, C303.2, C304.2, M301.2 (GND), M301.3 (MH), Q302.2 (S), T301.2, U301.10 (GND); also elsewhere on the board
/VCC: C303.1, Q301.2 (D), U301.8 (VCC), U301.11 (MODE_SYNC); also elsewhere on the board
/power/VAA: D301.2 (A), T301.1
/power/VBB: C301.1, C302.1, D301.1 (K), Q301.3 (S), R301.1, U301.2 (EN), U301.3 (VIN)
/power/~ENABLE_VCC: Q301.1 (G), R301.2, R302.1
unnamed: Q302.3 (D), R302.2

Board: 4 copper layers, 78 parts (6 on the bottom side), 54 nets, no tracks yet.

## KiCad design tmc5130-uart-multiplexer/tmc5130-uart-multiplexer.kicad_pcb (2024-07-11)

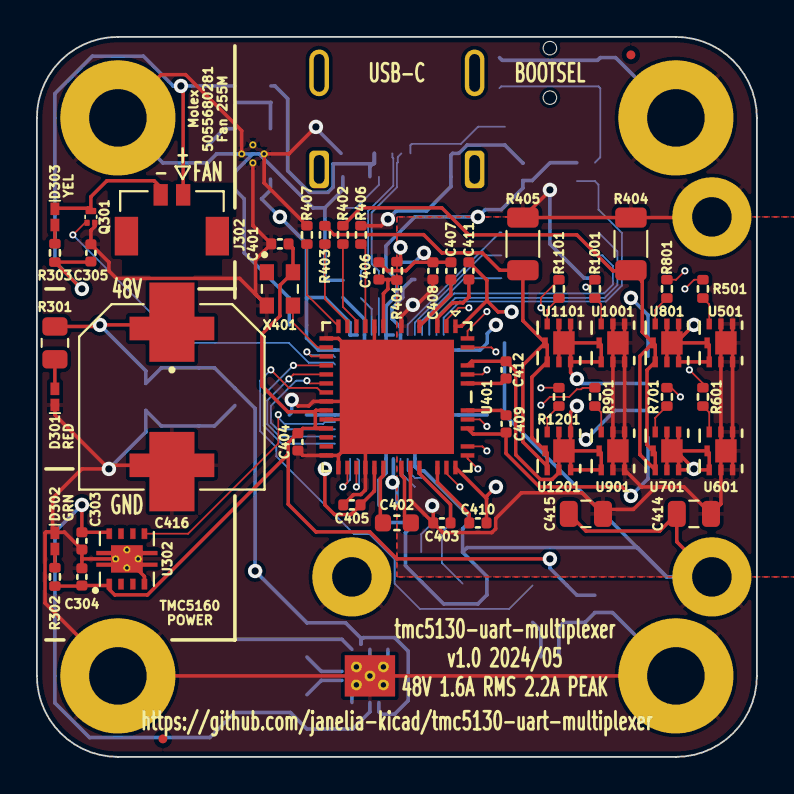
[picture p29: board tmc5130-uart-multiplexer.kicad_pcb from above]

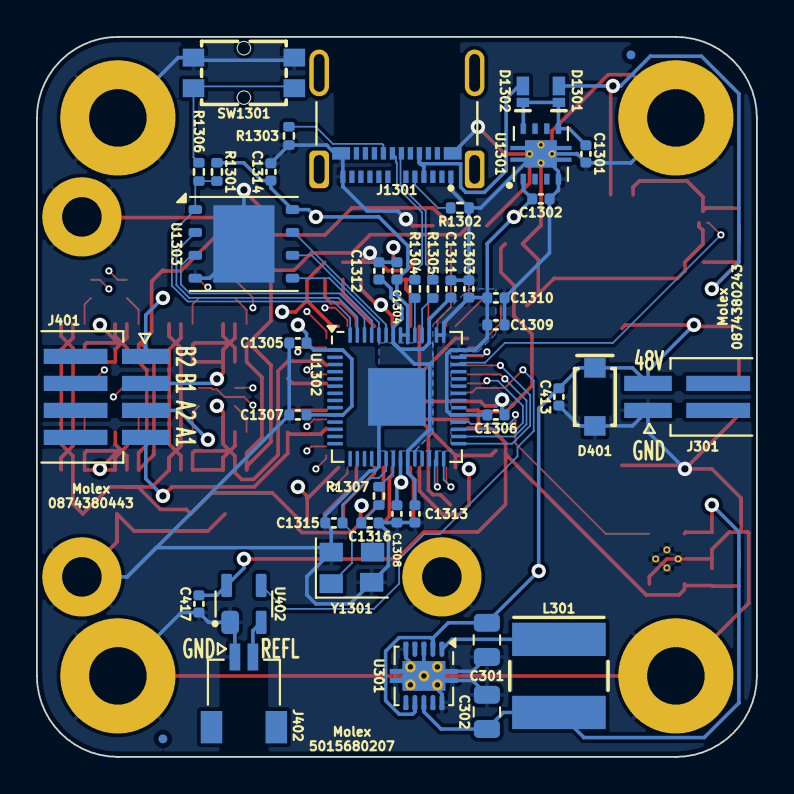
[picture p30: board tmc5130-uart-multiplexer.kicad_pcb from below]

Board: 4 copper layers, 40.0 x 40.0 mm, 103 parts (44 on the bottom side), 76 nets.

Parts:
C301, C414, C415: 2.2uF_100V; C_0805_2012Metric
C302: 47uF_10V; C_0805_2012Metric
C303, C304, C305, C1301, C1302: 1uF_25V; C_0402_1005Metric
C401, C403, C404, C408, C413, C417, C1304, C1305, C1306, C1307, C1308, C1309, C1310, C1312, C1313, C1314: 0.1uF_100V; C_0402_1005Metric
C402: 22nF_100V; C_0603_1608Metric
C405: 0.47uF_35V; C_0402_1005Metric
C406, C407: 2.2uF_35V; C_0402_1005Metric
C409, C410, C411, C412: 0.22uF_25V; C_0402_1005Metric
C416: 220uF_63V; CP_Hybrid_EEHZS1H221V
C1303, C1311: 1uF_35V; C_0402_1005Metric
C1315, C1316: 15pF_25V; C_0402_1005Metric
D301: LED_RED; LED_0402-1005_KNB
D302: LED_GRN; LED_0402-1005_KNB
D303: LED_YEL; LED_0402-1005_KNB
D401: D_Zener_48V_2.6A; SMFSeries_LTF
D1301, D1302: D_SCHOTTKY_40V_2A; CR_DSN2_152AB-C_OSI
FID201, FID202, FID203, FID204: FIDUCIAL_0.5mm_MASK1mm; FIDUCIAL_0.5mm_Mask1mm
H201, H202, H203, H204: MountingHole_M3_Pad; MountingHole_3.2mm_M3_Pad
J301: Molex_Pico-SPOX_Horizontal; Molex_Pico-SPOX-87438_1x02-P1.5mm_Horizontal
J302: Molex_Pico-Lock-PLUS_Vertical; Molex_Micro-Lock-PLUS-505568_1x02_P1.25mm_Vertical
J401: Molex_Pico-SPOX_Horizontal; Molex_Pico-SPOX-87438_1x04-P1.5mm_Horizontal
J402: Molex_Pico-Clasp_Horizontal; Molex_Pico-Clasp-501568_1x02_P1mm_Horizontal
J1301: Connector_USB_C_Receptacle; USB_C_Receptacle_Amphenol_10152803-00011LF
L301: 150uH_553mA; IND_CB_SD25
M301: Fan_5VDC_25x25x8mm; FAN_5VDC_25x25x8mm
Q301: MOSFET-N-CH; XFDFN-3
R301: 2.32k; R_0805_2012Metric
R302: 64.9; R_0402_1005Metric
R303: 249; R_0402_1005Metric
R401: 2.2; R_0402_1005Metric
R402, R403, R406, R407: 47; R_0402_1005Metric
R404, R405: 0.15; R_1206_3216Metric
R501, R601, R701, R801, R901, R1001, R1101, R1201: 15; R_0402_1005Metric
R1301: 10.0k; R_0402_1005Metric
R1302, R1303: 5.1k; R_0402_1005Metric
R1304, R1305: 27; R_0402_1005Metric
R1306, R1307: 1k; R_0402_1005Metric
SW1301: Switch_Tactile_SPST-NO_SMT_Side; SMT_1045822_WRE
U301: Switching_5V_500mA; Texas_S-PVSON-N10_ThermalVias
U302, U1301: Linear_3.3V_1A; TPS737Q1
U401: TMC5160A-WA; 21-100593_ADI
U402: MAX6816; SOT192P237X122-4N
U501, U601, U701, U801, U901, U1001, U1101, U1201: BUK7D36-60EX; BUK7D3660EX_NEX
U1302: MCU_RP2040; QFN-56-1EP_7x7mm_P0.4mm_EP3.2x3.2mm
U1303: Memory_Flash_W25Q128JVZPIQ; WSON-8-1EP_6x5mm_P1.27mm_EP3.4x4.3mm
X401: 16MHz; OSC_ECS-2520S33-160-FN-TR
Y1301: Crystal_12MHz; Crystal_SMD_Abracon_ABM8-4Pin_3.2x2.5mm

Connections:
/+5V: C302.1, C303.1, C305.1, D1301.2 (A), J302.1, L301.2, R303.1, U301.8 (VOUT), U302.8 (IN)
/DIAG0: U401.27 (SWN/DIAG0), U1302.28 (GPIO17)
/DIAG1: U401.28 (SWP/DIAG1), U1302.27 (GPIO16)
/ENABLE_FAN: Q301.1 (G), U1302.40 (GPIO28_ADC2)
/ENABLE_VIO: U302.5 (EN), U1302.32 (GPIO21)
/GND: C301.2, C302.2, C303.2, C304.2, C305.2, C401.2, C404.2, C405.2, C406.2, C407.2, C408.2, C413.2, C414.2, C415.2, C416.2, C417.2, C1301.2, C1302.2, C1303.2, C1304.2, C1305.2, C1306.2, C1307.2, C1308.2, C1309.2, C1310.2, C1311.2, C1312.2, C1313.2, C1314.2, C1315.2, C1316.2, D301.1 (K), D302.1 (K), D401.2 (A), H201.1, H202.1, H203.1, H204.1, J301.1, J402.1, J1301.A1 (GND), J1301.A12 (GND), J1301.B1 (GND), J1301.B12 (GND), M301.1, M301.2, M301.3, Q301.2 (S), R404.2, R405.2, R406.2, R407.2, R1302.2, R1303.2, SW1301.2, SW1301.4, U301.3 (ILIM), U301.5 (RT), U301.10 (GND), U301.11 (GND), U302.4 (GND), U302.9 (PAD), U401.7 (GNDA), U401.12 (TST_MODE), U401.19 (REFR/DIR), U401.21 (SD_MODE), U401.25 (GNDD), U401.26 (ENCN/DCO/CFG6), U401.29 (~DRV_EN), U401.48 (EP), U402.1 (GND), U1301.4 (GND), U1301.9 (PAD), U1302.19 (TESTEN), U1302.57 (GND), U1303.4 (GND), U1303.9 (EP), X401.2 (GND), Y1301.2, Y1301.4
/MISO: U401.17 (SDO/CFG0), U1302.31 (GPIO20)
/MOSI: U401.16 (SDI/CFG1), U1302.30 (GPIO19)
/SCK: U401.15 (SCK/CFG2), U1302.29 (GPIO18)
/VIO: C304.1, C401.1, C404.1, C417.1, R302.1, U302.1 (OUT), U401.20 (VCC_IO), U401.22 (SPI_MODE), U402.4 (Vcc), X401.4 (VDD)
/VM: C301.1, C403.1, C408.1, C413.1, C414.1, C415.1, C416.1, D401.1 (K), J301.2, R301.1, U301.2 (VIN), U301.7 (EN), U401.5 (VSA), U401.33 (VS), U501.1 (D), U501.2 (D), U501.5 (D), U501.6 (D), U501.7 (D), U601.1 (D), U601.2 (D), U601.5 (D), U601.6 (D), U601.7 (D), U901.1 (D), U901.2 (D), U901.5 (D), U901.6 (D), U901.7 (D), U1001.1 (D), U1001.2 (D), U1001.5 (D), U1001.6 (D), U1001.7 (D)
/power/FAN-: D303.1 (K), J302.2, Q301.3 (D)
/power/LED_GRN+: D302.2 (A), R302.2
/power/LED_RED+: D301.2 (A), R301.2
/power/LED_YEL+: D303.2 (A), R303.2
/power/SW: L301.1, U301.1 (SW)
/rp2040/+1.1V: C1311.1, C1312.1, C1313.1, U1302.23 (DVDD), U1302.45 (VREG_VOUT), U1302.50 (DVDD)
/rp2040/+3.3V: C1302.1, C1303.1, C1304.1, C1305.1, C1306.1, C1307.1, C1308.1, C1309.1, C1310.1, C1314.1, R1301.2, U1301.1 (OUT), U1302.1 (IOVDD), U1302.10 (IOVDD), U1302.22 (IOVDD), U1302.33 (IOVDD), U1302.42 (IOVDD), U1302.43 (ADC_AVDD), U1302.44 (VREG_IN), U1302.48 (USB_VDD), U1302.49 (IOVDD), U1303.8 (VCC)
/rp2040/CC1: J1301.A5 (CC1), R1302.1
/rp2040/CC2: J1301.B5 (CC2), R1303.1
/rp2040/D+: J1301.B6 (D+), R1304.1
/rp2040/D-: J1301.B7 (D-), R1305.1
/rp2040/QSPI_SCLK: U1302.52 (QSPI_SCLK), U1303.6 (CLK)
/rp2040/QSPI_SD0: U1302.53 (QSPI_SD0), U1303.5 (DI(IO0))
/rp2040/QSPI_SD1: U1302.55 (QSPI_SD1), U1303.2 (DO(IO1))
/rp2040/QSPI_SD2: U1302.54 (QSPI_SD2), U1303.3 (IO2)
/rp2040/QSPI_SD3: U1302.51 (QSPI_SD3), U1303.7 (IO3)
/rp2040/QSPI_SS: R1301.1, R1306.1, U1302.56 (QSPI_SS), U1303.1 (~CS)
/rp2040/USB_N: R1305.2, U1302.46 (USB_DM)
/rp2040/USB_P: R1304.2, U1302.47 (USB_DP)
/rp2040/VBUS: D1302.2 (A), J1301.A4 (VBUS), J1301.B9 (VBUS)
/rp2040/VSYS: C1301.1, D1301.1 (K), D1302.1 (K), U1301.5 (EN), U1301.8 (IN)
/rp2040/XIN: C1315.1, U1302.20 (XIN), Y1301.1
/rp2040/XOUT: R1307.1, U1302.21 (XOUT)
/rp2040/XOUTB: C1316.1, R1307.2, Y1301.3
/rp2040/~USB_BOOT: R1306.2, SW1301.1, SW1301.3
/tmc5160/5VOUT: C406.1, R401.2, U401.6 (5VOUT)
/tmc5160/12VOUT: C407.1, U401.4 (12VOUT)
/tmc5160/BMA1: C409.2, J401.4, U401.40 (BMA1), U501.4 (S), U501.8 (S), U801.1 (D), U801.2 (D), U801.5 (D), U801.6 (D), U801.7 (D)
/tmc5160/BMA2: C410.2, J401.3, U401.37 (BMA2), U601.4 (S), U601.8 (S), U701.1 (D), U701.2 (D), U701.5 (D), U701.6 (D), U701.7 (D)
/tmc5160/BMB1: C411.2, J401.2, U401.1 (BMB1), U1001.4 (S), U1001.8 (S), U1101.1 (D), U1101.2 (D), U1101.5 (D), U1101.6 (D), U1101.7 (D)
/tmc5160/BMB2: C412.2, J401.1, U401.45 (BMB2), U901.4 (S), U901.8 (S), U1201.1 (D), U1201.2 (D), U1201.5 (D), U1201.6 (D), U1201.7 (D)
/tmc5160/CA1: C409.1, U401.42 (CA1)
/tmc5160/CA2: C410.1, U401.35 (CA2)
/tmc5160/CB1: C411.1, U401.3 (CB1)
/tmc5160/CB2: C412.1, U401.43 (CB2)
/tmc5160/CLOCK: U401.13 (CLK), X401.3 (OUT)
/tmc5160/CPI: C402.2, U401.32 (CPI)
/tmc5160/CPO: C402.1, U401.31 (CPO)
/tmc5160/HA1: R501.1, U401.41 (HA1)
/tmc5160/HA2: R601.1, U401.36 (HA2)
/tmc5160/HB1: R1001.1, U401.2 (HB1)
/tmc5160/HB2: R901.1, U401.44 (HB2)
/tmc5160/LA1: R801.1, U401.39 (LA1)
/tmc5160/LA2: R701.1, U401.38 (LA2)
/tmc5160/LB1: R1101.1, U401.47 (LB1)
/tmc5160/LB2: R1201.1, U401.46 (LB2)
/tmc5160/REFL: J402.2, U402.2 (IN)
/tmc5160/REFL_DEBOUNCED: U401.18 (REFL/STEP), U402.3 (OUT)
/tmc5160/SRA: R402.2, R404.1, U701.4 (S), U701.8 (S), U801.4 (S), U801.8 (S)
/tmc5160/SRAH: R402.1, U401.9 (SRAH)
/tmc5160/SRAL: R406.1, U401.8 (SRAL)
/tmc5160/SRB: R403.2, R405.1, U1101.4 (S), U1101.8 (S), U1201.4 (S), U1201.8 (S)
/tmc5160/SRBH: R403.1, U401.10 (SRBH)
/tmc5160/SRBL: R407.1, U401.11 (SRBL)
/tmc5160/VCC: C405.1, R401.1, U401.30 (VCC)
/tmc5160/VCP: C403.2, U401.34 (VCP)
/tmc5160/mosfet1/GATEB: R501.2, U501.3 (G)
/tmc5160/mosfet2/GATEB: R601.2, U601.3 (G)
/tmc5160/mosfet3/GATEB: R801.2, U801.3 (G)
/tmc5160/mosfet4/GATEB: R701.2, U701.3 (G)
/tmc5160/mosfet5/GATEB: R1001.2, U1001.3 (G)
/tmc5160/mosfet6/GATEB: R901.2, U901.3 (G)
/tmc5160/mosfet7/GATEB: R1101.2, U1101.3 (G)
/tmc5160/mosfet8/GATEB: R1201.2, U1201.3 (G)
/~CS: U401.14 (~CS/CFG3), U1302.41 (GPIO29_ADC3)

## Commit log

2024-06-28 Deleted unused schematics
    [assembly.kicad_sch, mosfet.kicad_sch, power.kicad_sch, rp2040.kicad_sch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]
2024-07-02 Update components
    [tmc51x0-multiplexer-uart.kicad_sch]
2024-07-09 Add components
    [power.kicad_sch]
2024-07-10 Change sheets
    [assembly.kicad_sch, microcontroller.kicad_sch, motor.kicad_sch, power.kicad_sch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]
2024-07-11 tmc51x0-multiplexer-uart -> tmc5130-uart-multiplexer
    [assembly.kicad_sch, microcontroller.kicad_sch, motor.kicad_sch, power.kicad_sch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]
2024-07-11 Fix some design rule checks
    [microcontroller.kicad_sch, motor.kicad_sch, power.kicad_sch, tmc5130-uart-multiplexer.kicad_sch]
2024-07-12 tmc5130-uart-multiplexer -> honeycomb-pcb
    [assembly.kicad_sch, honeycomb-pcb.kicad_pcb, honeycomb-pcb.kicad_sch, microcontroller.kicad_sch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]
2024-07-12 motor -> prism
    [assembly.kicad_sch, honeycomb-pcb.kicad_pcb, honeycomb-pcb.kicad_sch, microcontroller.kicad_sch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]
2024-07-16 Update BOM
    [assembly.kicad_sch, honeycomb-pcb.kicad_sch, jlcpcb-bom.csv, microcontroller.kicad_sch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]
2024-07-16 Last update before renaming
    [honeycomb-pcb.kicad_pcb, jlcpcb-bom.csv, microcontroller.kicad_sch, power.kicad_sch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]
2024-07-16 honeycomb-pcb -> cluster-pcb
    [assembly.kicad_sch, cluster-pcb.kicad_pcb, cluster-pcb.kicad_sch, microcontroller.kicad_sch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]
2024-07-16 Initial layout
    [cluster-pcb.kicad_pcb, cluster-pcb.kicad_sch, microcontroller.kicad_sch, power.kicad_sch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]
2024-07-18 Add tracks
    [cluster-pcb.kicad_pcb]
2024-07-25 Add some more traces
    [cluster-pcb.kicad_pcb]
2024-07-26 Finalize layout
    [assembly.kicad_sch, cluster-pcb.kicad_pcb, cluster-pcb.kicad_sch, microcontroller.kicad_sch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]
2024-07-26 Update metadata
    [cluster-pcb-B_Cu.gbl, cluster-pcb-B_Fab.gbr, cluster-pcb-B_Mask.gbs, cluster-pcb-B_Paste.gbp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]
2024-08-20 First steps towards v1.1
    [assembly.kicad_sch, cluster-pcb.kicad_pcb, cluster-pcb.kicad_sch, microcontroller.kicad_sch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]
2024-08-26 Update to version 1.1
    [assembly.kicad_sch, cluster-pcb.kicad_pcb, cluster-pcb.kicad_sch, microcontroller.kicad_sch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]
2024-08-26 Update documentation
    [cluster-pcb-B_Cu.gbl, cluster-pcb-B_Fab.gbr, cluster-pcb-B_Mask.gbs, cluster-pcb-B_Paste.gbp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]
2024-08-30 Add documentation
    [cluster-pcb.kicad_sch]
2024-08-30 Add address
    [address.kicad_sch, assembly.kicad_sch, cluster-pcb.kicad_sch, microcontroller.kicad_sch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]
2024-09-03 Add i2c pullups
    [cluster-pcb.kicad_sch, microcontroller.kicad_sch]
2024-09-10 100 -> 120 ohm and change connectors
    [address.kicad_sch, assembly.kicad_sch, cluster-pcb.kicad_sch, microcontroller.kicad_sch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]
2024-09-10 Adjust schematic
    [prism.kicad_sch]
2024-09-12 Update schematic
    [address.kicad_sch, assembly.kicad_sch, audio.kicad_sch, cluster-pcb.kicad_sch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]
2024-09-13 Fix ERC issues
    [address.kicad_sch, assembly.kicad_sch, audio.kicad_sch, cluster-pcb.kicad_sch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]
2024-09-13 Rearrange footprints
    [cluster-pcb.kicad_pcb, prism.kicad_sch]
2024-09-13 Routed most tracks
    [cluster-pcb.kicad_pcb, microcontroller.kicad_sch, multiplexer.kicad_sch]
2024-09-13 Update to version 1.2
    [cluster-pcb-B_Cu.gbl, cluster-pcb-B_Fab.gbr, cluster-pcb-B_Mask.gbs, cluster-pcb-B_Paste.gbp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]
2024-09-20 First SPI changes
    [address.kicad_sch, assembly.kicad_sch, audio.kicad_sch, cluster-pcb.kicad_sch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]
2024-09-27 Progress toward v2.0
    [cluster-pcb.kicad_sch, microcontroller.kicad_sch, prism.kicad_sch]
2024-09-27 Initial pcb layout
    [address.kicad_sch, assembly.kicad_sch, audio.kicad_sch, cluster-pcb.kicad_pcb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]
2024-09-27 Adjust solder pads
    [cluster-pcb.kicad_pcb]
2024-09-30 Progress towards layout
    [address.kicad_sch, assembly.kicad_sch, audio.kicad_sch, cluster-pcb.kicad_pcb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]
2024-09-30 Update routing
    [cluster-pcb.kicad_pcb, cluster-pcb.kicad_sch, microcontroller.kicad_sch, prism.kicad_sch]
2024-10-01 Finish routing
    [address.kicad_sch, assembly.kicad_sch, audio.kicad_sch, cluster-pcb.kicad_pcb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]
2024-10-01 Finish v2.0
    [cluster-pcb-B_Cu.gbl, cluster-pcb-B_Fab.gbr, cluster-pcb-B_Mask.gbs, cluster-pcb-B_Paste.gbp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]
2024-10-21 Progress toward schematic v2.1
    [address.kicad_sch, assembly.kicad_sch, audio.kicad_sch, cluster-pcb.kicad_sch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]
2024-10-22 Finished v2.1
    [address.kicad_sch, assembly.kicad_sch, audio.kicad_sch, cluster-pcb-B_Cu.gbl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]
2025-05-23 Update kicad to version 9
    [address.kicad_sch, assembly.kicad_sch, audio.kicad_sch, cluster-pcb.kicad_pcb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]
